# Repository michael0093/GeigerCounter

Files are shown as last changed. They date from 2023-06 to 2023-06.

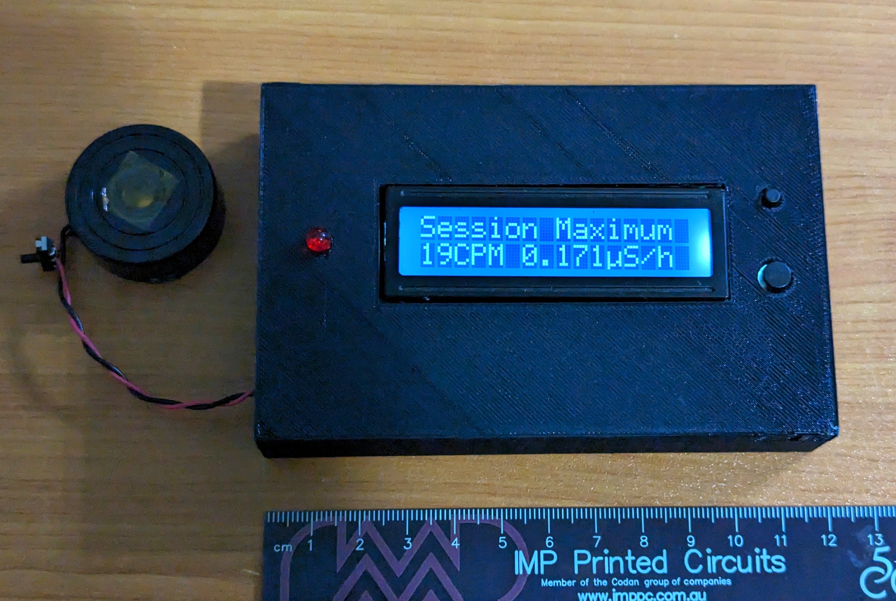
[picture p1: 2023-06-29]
Photos/PXL_20230629_101145013.jpg

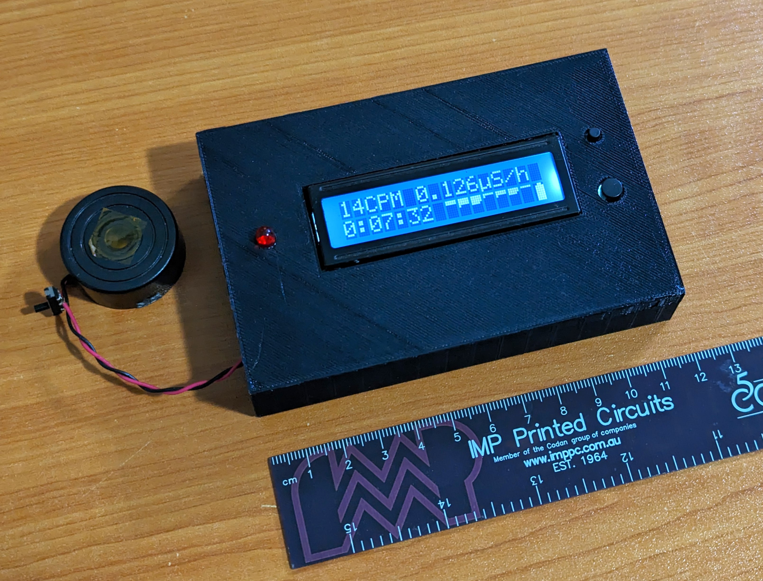
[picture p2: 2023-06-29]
Photos/PXL_20230629_101126934.jpg

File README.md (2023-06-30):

# Summary
CBM20 Geiger counter using PIC16F88 and 16x2 LCD

# Features
- Displays current CPM and dose (uS/hr) with rolling graph of last-seven time blocks
- Screens for session maximum and average, and all-time maximum CPM/dose
- Elapsed time display
- Rechargeable 18650 with charge level indicator
- Integration time of 60s or 10s
- Digital-loop boost converter with fault detection
- Audible and visual indicator

# Building
MPLABX v6.05 with XC8 compiler v2.36 optimisation 02s
3060 of 4096 bytes code space.

# Schematic

Drawing TBA, general overview: 18650 into eBay power bank module, whose 5V output goes into the system. Power switch is DPDT so that 5V to CPU and cell voltage (for measurement) gets cut. Boost converter is NFET driven by CPU, with 330uF polymer and ceramics at input, a few HV MLCCs at output. Feedback into CPU via big resistor divider. Two big resistors into CBM20 tube. The other side of the tube is connected to a sense circuit similar to the ones in the references.
LCD/Buzzer/LED/BoostFET all powered directly from power bank module's 5V output. The CPU is powered via 33R resistor and 1000uF electrolytic so that the dips due to the power bank module don't interfere much with the ADC performance.

# Pinning
Name | Description
-----|-----------
A0   | HV Feedback
A1   | Vbatt
A2   | Backlight
A3   | -	
A4   | -
A5   | -
A6	 | LCD-Reg
A7	 | LCD-Enable
B0	 | Boost (PWM)
B1	 | LCD-Data
B2	 | LCD-Data
B3	 | [PGM] LCD-Data
B4   | LCD-Data
B5   | Tube
B6   | PGC / Buzzer/LED
B7   | PGD / Button

# Detailed Operation

Upon power up the firmware version is shown and a lamp/buzzer test occurs. If the screen button is unpressed at power-up then the default integration time of 60 seconds is used. This means that each time block and CPM/does is calculated every 60s. If the button is held during power-up the startup screen will show Intg=10s meaning that each time block is only 10s. This gives a faster moving graph and more frequently updating readings, however it is less accurate.
The main screen at the top shows the CPM and dose in uS/hr, these values are updated every integration time. The lower left shows the total run time in H:MM:SS, and the far right shows a battery charge indicator with seven states. To the left of the battery indicator is a graph area with seven blocks which record the counts in each integration time. This graph fills from the top-down and always shows the counts for the last seven times. 
On the main screen, holding the button will reset the run time to zero, without affecting the current counts or the graph. 
A shorter press of the button will advance to the next screen which shows the maximum recording for this power-on session. Holding the button on this screen resets the session maximum to zero with affecting any other parameters.
A shorter press of the button will advance to the next screen which shows the average recording for this power-on session. Holding the button on this screen resets the session average to zero with affecting any other parameters.
A shorter press of the button will advance to the next screen which shows the maximum recording ever attained. This value is recorded in EEPROM and persists through power cycling. Holding the button on this screen resets the all-time maximum to zero with affecting any other parameters.
A shorter press of the button will return to the main screen again.
If the code restarts due to a watchdog timer reset, a 'w' is shown between the run time and graph to warn the user that the readings may not be complete.
The firmware detects over/under voltage regulation of the high voltage, as well as if the firmware attempts to drive the FET gate with too high a duty cycle for a continuous period. In these cases all operation will cease and the display shows "HV OVER ERROR", "HV UNDER ERROR" or "HV DUTY ERROR" respectively. 

# Known Issues / ToDo
- Produce schematic

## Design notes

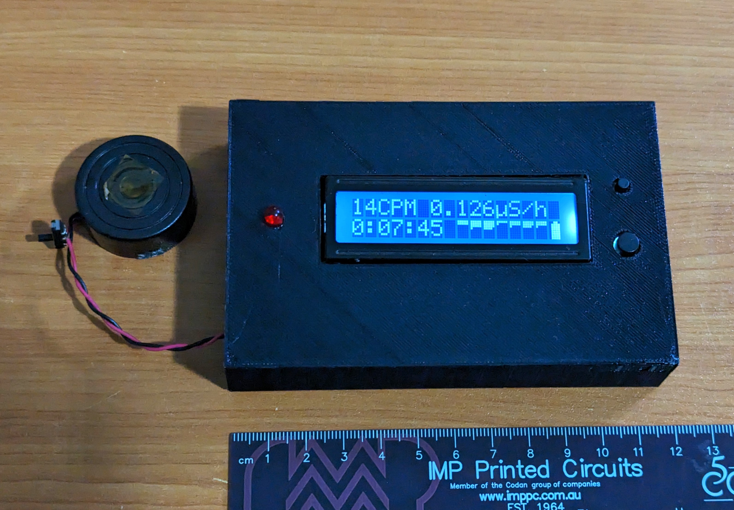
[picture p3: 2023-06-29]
Photos/PXL_20230629_101139840.MP.jpg

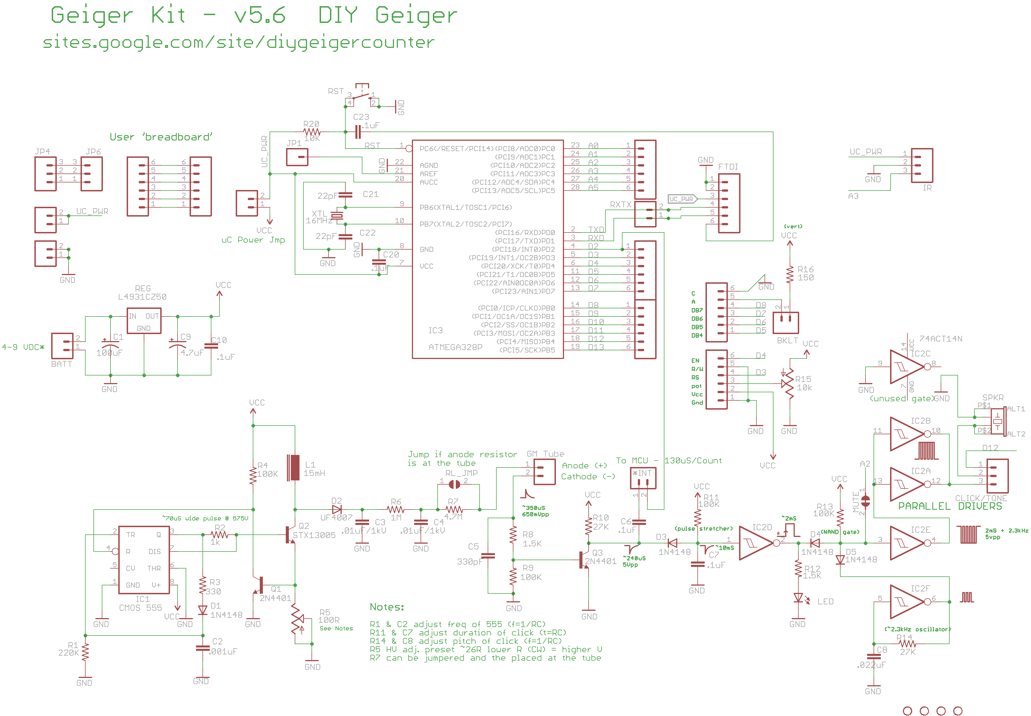
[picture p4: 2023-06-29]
References/geiger.png

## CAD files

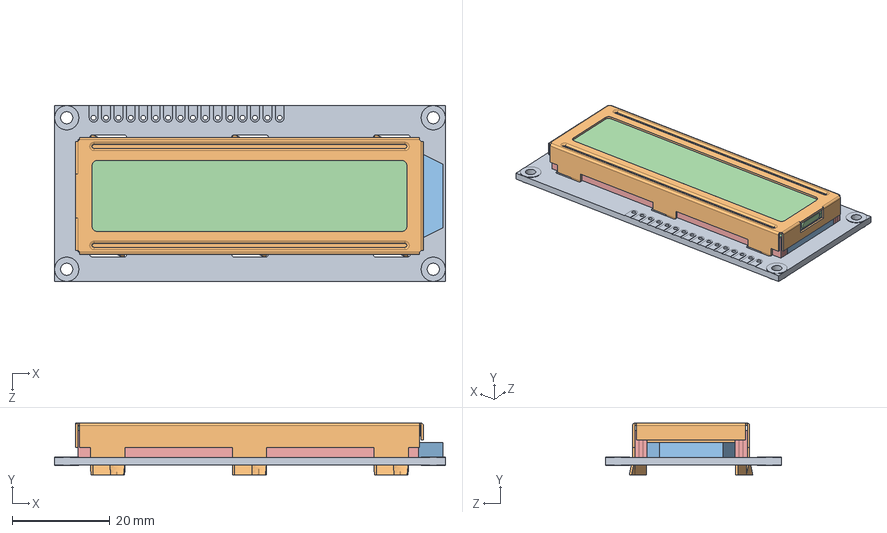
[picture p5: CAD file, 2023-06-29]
Mechanical/DFRobot_1602_LCD.SLDASM
80.0 x 10.6 x 36.0 mm
LCD_PCB
metal_casing
LCDbacklight
LCD
conductors x 2

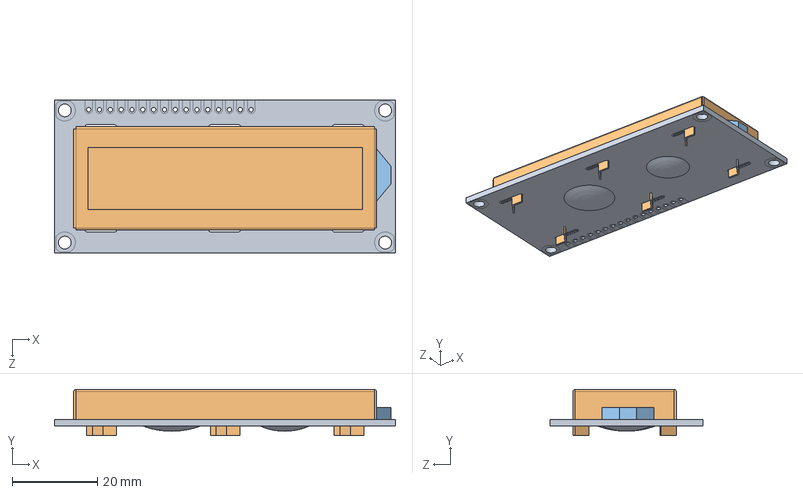
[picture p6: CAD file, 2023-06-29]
Mechanical/LCD_ASM.SLDASM
80.0 x 10.8 x 36.0 mm
LCD_board
LCD_screen
LCD_backlight

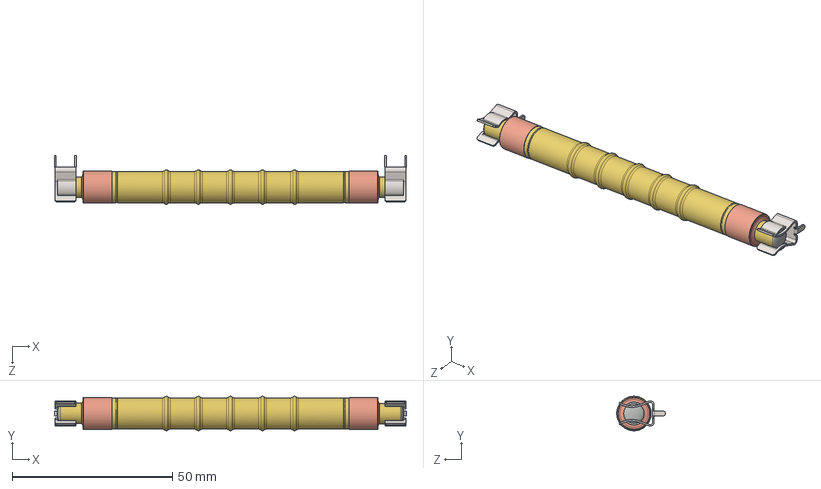
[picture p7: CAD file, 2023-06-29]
Mechanical/SBM-20.STEP
109.8 x 10.8 x 15.2 mm
SBM-20_tybe
ч蜱齁罻 x 2
Êîíòàêò x 2
fuse_holder_6_30 x 2

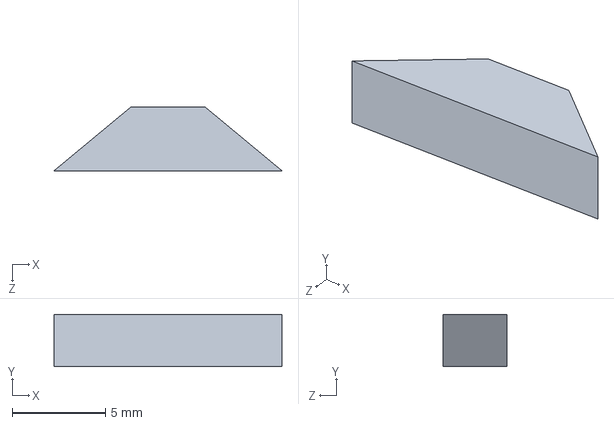
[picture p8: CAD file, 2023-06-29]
Mechanical/LCD_backlight.SLDPRT
12.2 x 2.80 x 3.40 mm

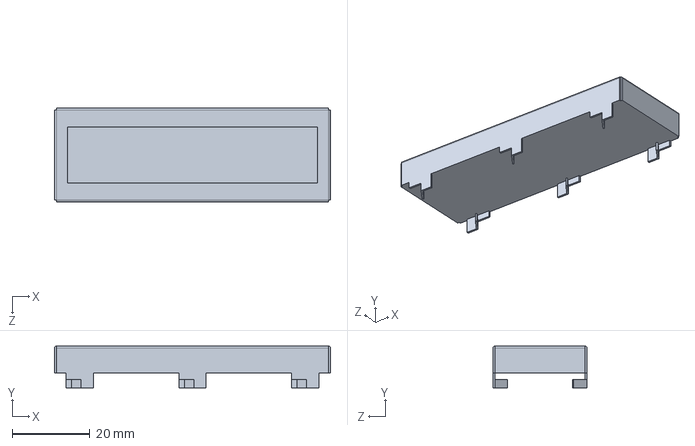
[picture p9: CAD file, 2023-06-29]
Mechanical/LCD_screen.SLDPRT
71.1 x 10.8 x 24.3 mm

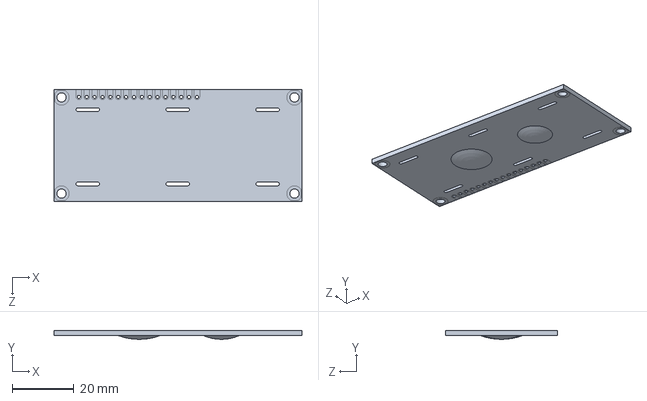
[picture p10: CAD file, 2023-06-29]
Mechanical/LCD_board.SLDPRT
80.0 x 2.81 x 36.0 mm

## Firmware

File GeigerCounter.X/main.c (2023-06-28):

/*
 * File:   main.c
 * Author: MichaelC
 *
 * Created on August 8, 2021, 3:05 PM
 */

// CONFIG1
#pragma config FOSC = INTOSCIO  // Oscillator Selection bits (INTRC oscillator; port I/O function on both RA6/OSC2/CLKO pin and RA7/OSC1/CLKI pin)
#pragma config WDTE = ON        // Watchdog Timer Enable bit 
#pragma config PWRTE = ON       // Power-up Timer Enable bit (PWRT enabled)
#pragma config MCLRE = ON      // RA5/MCLR/VPP Pin Function Select bit 
#pragma config BOREN = ON       // Brown-out Reset Enable bit (BOR enabled)
#pragma config LVP = OFF        // Low-Voltage Programming Enable bit (RB3/PGM pin has RB3 function, LVP disabled)
#pragma config CPD = OFF        // Data EE Memory Code Protection bit (Code protection off)
#pragma config WRT = OFF        // Flash Program Memory Write Enable bits (Write protection off)
#pragma config CCPMX = RB0      // CCP1 Pin Selection bit (CCP1 function on RB0)
#pragma config CP = OFF         // Flash Program Memory Code Protection bit (Code protection off)

// CONFIG2
#pragma config FCMEN = ON       // Fail-Safe Clock Monitor Enable bit (Fail-Safe Clock Monitor enabled)
#pragma config IESO = ON        // Internal External Switchover bit (Internal External Switchover mode enabled)
    
#include <xc.h>

#define _XTAL_FREQ          8000000

#define ADC_TMR0_RATE       100//210     // Timer0 is Fosc/4/8: up to 1.024ms. (256-206 = rate 200us))
#define TMR1_CLOCK_RATE_H   0x9E    // Timer1 is Fost/4/8: up to 0.262s. (65536-40536 = Rate = 0.1s)
#define TMR1_CLOCK_RATE_L   0x40


#define EVENT_HVFB          0b10000000      // Interrupt driven events
#define EVENT_VBATT         0b01000000
#define EVENT_PORTB         0b00100000
#define EVENT_100ms         0b00010000

// 5x8 display supports battery capacitor symbol 0-6 (7 states)
// Calculation is V*1023 / 5180. VDD=5.106V but 5.18V gives more accuracte test results
#define V_SUPPLY            4995                // VDD of CPU when running from battery booster
#define ADCRES              1023
#define VBATT_6of6          (((4050)/V_SUPPLY)*ADCRES)   // >4.05V
#define VBATT_5of6          (((3950)/V_SUPPLY)*ADCRES)   // >3.95V
#define VBATT_4of6          (((3850)/V_SUPPLY)*ADCRES)   // >3.85V
#define VBATT_3of6          (((3800)/V_SUPPLY)*ADCRES)   // >3.80V
#define VBATT_2of6          (((3780)/V_SUPPLY)*ADCRES)   // >3.78V
#define VBATT_1of6          (((3720)/V_SUPPLY)*ADCRES)   // >3.72V
#define VBATT_0of6          (((3640)/V_SUPPLY)*ADCRES)   // >3.64

#define LCD_RS              PORTAbits.RA6  // RA6 LCD RS Pin
#define LCD_E               PORTAbits.RA7  // RA7 LCD E Pin
#define LCD_DB4             PORTBbits.RB4  // RB4 LCD 4 Pin
#define LCD_DB5             PORTBbits.RB3  // RB3 LCD 5 Pin
#define LCD_DB6             PORTBbits.RB2  // RB2 LCD 6 Pin
#define LCD_DB7             PORTBbits.RB1  // RB1 LCD 7 Pin
#define LCD_DELAY           5       // General delay between commands. 1us works, 40us as long as you'd ever need

#define EEWRITE_TIMEOUT     8       // x1ms
#define ALLTIMEMAX_EEADDR   0       // EEPROM address of alltime max, MSByte, LSByte is +1 from this

#define TARGET_HVFB         689     // 6M6/56k divider so (5* TARGET_HVFB/1023) / (56k / (56k+6M6)) eg 689 counts = 400V
#define CURRERROR_LIMIT     35      // +/- this from target above causes error
#define ERR_ACCUMTIME       50      // Main loop cycles before system stop due to HV error
#define ERR_ACCUMDUTY       200     // Int loop cycles before system stop due to HV duty error
#define HV_DUTY_MAX         180     // 100% duty = PR2<<2 value. eg 224/(80<<2) = 70%. typ=150
#define DEFAULT_PID_P       10      // Divided factor
#define DEFAULT_PID_D       0       // Multiplied factor       

#define uSV_DECIMALS        3       // Show uSV conversion to this many decimal places
#define CPM_uSV             900//632    
#define CPM_uSV_DIV         100000  // uSv/h = CPM * CPM_uSV / CPM_uSV_
#define CPM_MAX             9999
#define FAST_COUNT_TIME     100     // x0.1s CPM calculation time window (update rate)
#define SLOW_COUNT_TIME     600     // x0.1s CPM calculation time window (update rate)
#define BATT_TIME           5       // x0.1s Battery symbol update rate

#define COUNTS_PER_PIXEL    1
#define BLOCK_X             5       // Each HD44780 block is 5x7 pixels
#define BLOCK_Y             8
#define PIXELS_PER_BLOCK    (BLOCK_X*BLOCK_Y)   
#define COUNTS_PER_BLOCK    (COUNTS_PER_PIXEL*PIXELS_PER_BLOCK)

#define FAST_COUNT_TIME_MULT (600/FAST_COUNT_TIME)            // Multiply the counts within the COUNT_TIME to get CPM. 600 = 60sec in 0.1s
#define SLOW_COUNT_TIME_MULT 1            // Multiply the counts within the COUNT_TIME to get CPM. 600 = 60sec in 0.1s
#define FAST_COUNTS_MAX      (CPM_MAX/FAST_COUNT_TIME_MULT)   // Stop counting after this many within the COUNT_TIME
#define SLOW_COUNTS_MAX      (CPM_MAX/SLOW_COUNT_TIME_MULT)   // Stop counting after this many within the COUNT_TIME
//#define CPM_uS_SCALE        50       // multiply CPM by this to get uS/hr

#define BTN_PRESS_100ms     2       // Number of 0.1s before registering button press. "2" could be as short as 100ms and as long as 200ms
#define BTN_HOLD_100ms      20      // Number of 0.1s before registering button long-press. Max = 25
#define BL_TIMEOUT          6000    // x0.1s max is 65535. So 6,000 = 10 minutes

//    A0(an)	HVFB
//    A1(an)	Vbatt
//    A2(an)	Backlight
//    A3(an)	-
//    A4(an)	-
//    A5(in)	MCLR
//    A6	LCD-RS
//    A7	LCD-Enable
//    B0	Boost (PWM)
//    B1	LCD-Data
//    B2	LCD-Data
//    B3	[PGM] LCD-Data
//    B4(ioc)	LCD-Data
//    B5(ioc)	Tube
//    B6(ioc)	PGC / Buzzer/LED
//    B7(ioc)	PGD / Button

volatile uint8_t  btn     = 255;
volatile uint16_t vbatt   = 0;
volatile uint16_t hvfb    = 0;
volatile uint16_t counts  = 0;
volatile uint16_t newCnt  = 0;        // =1 when count has increased
volatile uint8_t tick_100ms = 0;
volatile uint8_t errDuty = 0;
volatile uint8_t displayState = 0;    // 0: normal screen. 1: session max. 2: alltime max

uint8_t errOver = 0;          // Even though many of these vars could be declared in the main() that increases code size a little, don't know why..
uint8_t errUndr = 0;
uint16_t cpm = 0;
uint32_t usv = 0;
uint8_t  countsArray[7] = {0};
uint8_t  numStr[8];
uint8_t  j;
uint8_t  graphBlock = 0;
uint16_t sessionHigh = 0;
uint32_t sessionSum  = 0;
uint16_t sessionTime = 0;
uint16_t alltimeHigh;
uint16_t intg_time;
uint8_t  count_mult;
uint8_t  wdtr = 0;
uint32_t runtime = 0;        // in 100ms increments
uint16_t bl_timeout = BL_TIMEOUT;

//volatile uint8_t dbg = 0;

uint8_t  HV_Startup_Duty = 0;
uint16_t count_max;

//void nop_delay(volatile uint16_t nops);
void lcd_init();
void lcd_clear();
void lcd_cursor(uint8_t row, uint8_t column);
void lcd_write_byte(uint8_t byteIn, uint8_t RS);
void lcd_write_nibble(uint8_t byteIn, uint8_t RS);
void lcd_write_string(uint8_t *stringArray);

void EEPROM_write(uint8_t data, uint8_t addr);
uint8_t EEPROM_read(uint8_t addr);

void clear_graph();
void recalc_graph();
uint8_t numDigits(uint32_t num);
uint8_t intToString(uint32_t number, uint32_t divisor, uint8_t* dest, uint8_t fixedWidth, uint8_t reduceDecimals);    // Convert long to null terminated string. When divisor=1, you get exactly what you put in

void batt_update();

void main(void) {
    // Peripheral Setup
    OSCCON = 0b01111100;    // 8MHz internal osc  
    
    PORTA  = 0b00000100;
    TRISA  = 0b00100011;    // HVFB and Vbatt inputs, A5 can only be input (MCLR)
    PORTB  = 0b01000000;    // Start with LED/buzzer on (to test)
    TRISB  = 0b10100000;    // Tube, Button inputs
    
    ANSEL  = 0b00000011;    // HVFB and Vbatt analog in
    ADCON1 = 0b10000000;    // Right justified data
    ADCON0 = 0b11000001;    // ADC clock = Fosc/32, 4us typical, turn on now
    
    OPTION_REG = 0b11000010; // Timer0 is Fosc/4/8: up to 1.024ms
    TMR0   = ADC_TMR0_RATE;  
    
    T1CON  = 0b00110001;    // Timer1 is Fost/4/8: up to 0.262s
    TMR1H  = TMR1_CLOCK_RATE_H;   
    TMR1L  = TMR1_CLOCK_RATE_L;
        
    WDTCON = 0b00000101;    // 4.096ms watchdog timeout, prescaler is used on Timer0
    
    PR2    = 80;            // 24.69kHz PWM period
    T2CON  = 0b00000100;    // TMR2 (PWM) on, period = Fosc/4/1
    CCPR1L = 0;
    CCP1CON = 0b00001100;   // PWM mode, this byte has 2LSBs (0b00XX0000)
    
    PIR1   = 0b00000000;
    PIE1   = 0b01000001;    // ADC and Timer1 interrupts
    INTCON = 0b11101000;    //0b11101000;    // Global interrupts enabled, PortB Change interrupt enabled

    // Welcome screen with version
    lcd_init();
    lcd_write_string("  GEIGER V1.0  ");
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
